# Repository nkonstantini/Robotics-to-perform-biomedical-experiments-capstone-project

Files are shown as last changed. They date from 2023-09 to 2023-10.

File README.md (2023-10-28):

# Robotics-to-perform-biomedical-experiments-capstone-project (PADL v2)
This repository contains all the design files, firmware modifications, and code used for this capstone project in order for you to replicate our work and design your own PADL v2 system.

## Folders:

Build instructions
-  This includes the Bill of Materials used in this project, as well as any tools required.
- This contains the full instructions in order to build this design yourself.

STL files
- This contains all the ready-to-print Fusion360 files we have used in the design.
- Some parts have been sourced from Sukukumar (2023) and [stratop80 (2015)](https://www.thingiverse.com/thing:1071695/files)

CAD files
- This contains all the CAD files we used (.f3d), in case you wish to modify the design. Note that we do not have all the STL files available as CAD files.

Laser cut files
- This contains the file for all the laser-cut parts in 3 different file types (.pdf, .dxf and .cdr)

Marlin firmware
- This contains the necessary instructions to reflash and modify the Marlin firmware on your Ender-3. There is an option to just download the firmware configuration we used if you do not wish to do this yourself.

Python files
- This contains Python files that can generate and export G-code for beginners.
- This contains Python files that can capture the webcam output.

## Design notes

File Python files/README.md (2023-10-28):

# Python code 
- This contains Python files that can generate and export G-code for beginners.
- This contains Python files that can capture the webcam output.

## Download python 3.11.5
https://www.python.org/downloads/ 

## Pip packages to download
Installation notes
To run this notebook you will need to install several packages, including Voila and Pygcode.

1. Voila can be installed via Conda: linked reference
conda install -c conda-forge voila
or with pip:
pip install voila

2. Python-Gcode can be installed via pip only: linked reference
pip install pygcode

3. Python widgets can be installed via pip only: linked reference
pip install ipywidgets

## Overall Flow Chart


## Detailed description
PADL: G-Code Generation Tool, is an innovative solution comprising six distinct components, each equipped with open-source Python code and libraries. The entire toolset is available for download on GitHub, allowing users the freedom to modify and enhance the codebase. This flexibility empowers future capstone students and researchers to update existing code and implement new features, thereby contributing to the continuous improvement of the tool.

0. Set Up
This section provides instructions and resources to set up the environment, including the installation of necessary Python packages such as Voila, PyGCode, and IPyWidgets for the PADL: G-Code Generation Tool (Figure 21).



1. Initialise Input Coordinates
The tool is compatible with all well plate configurations, with the option to input the number of columns, rows, and appropriate spacing between each well. The A1 well plate cell coordinates are measured using the Ender 3 XYZ coordinates, such as A1 = X65 Y154 Z12, prior to the input coordinates step. Additionally, the X step, for example, is measured as 9 (from A2 = X74 Y154 Z12), and the Y step size is measured as -9 (from B1 = X65 Y145 Z12) using the Ender-3 absolute coordinate system. Since equal spacing applies to all well plate cells, coordinates can be derived in subsequent steps. 

The tool facilitates the input of precise coordinates, ensuring accurate positioning, dispensing, and labelling of samples. Researchers can initialise the system for tailored experiments with desired coordinates, such as water reservoir and initial A1 coordinates, as depicted in Figure 22. 

It is worth noting that the use of JSON packages includes the local storage of desired coordinates. Researchers need to set up the coordinates only once, and the information will be automatically saved on their computers. The tool will start from the previously saved coordinates the next time it is opened. Users must refresh the page after making any modifications to ensure they are applied.



2. Speed Settings
A speed slider interface has been implemented, enabling users to control the movement speed of the x-carriage plate when retrieving liquid from the reservoir, the speed when transitioning between different well-plate cells, and the dispensing and aspirating speeds for liquid dispensing and withdrawal, respectively. Additionally, three waiting times have been added: between well-plate cells, between sub-experiments, and the initial waiting time. This control is facilitated using a JSON package as mentioned earlier and illustrated in Figure 23. This feature allows users to adjust the speed parameters for the needles in the syringe pump system, enhancing the precision and efficiency of the PADL system according to specific experimental requirements.



3. Get Well-Plate Coordinates
To optimise sample handling, the tool automatically retrieves well-plate coordinates as shown in Figure 24, from the data provided in Step 1. To verify the accuracy of the generated cooridnates, users must measure the coordinates for well H12. By comparing the actual coordinates to the ones generated automatically, users can confirm if the spacing and initial coordinates have been correctly set up and calibrated. If not, the necessary changes can be made to Step 1. Hence, manual calibration procedures are reduced, reducing manual errors and enhancing the overall efficiency of the PADL system.



4. Establish G-Code Commands for Sample Setup
The tool enables the selection of well-plate cells, displayed as buttons that can be clicked on. For example, a 96-well plate with rows 1-12 and columns A to H will be displayed as 96 buttons. Users can then choose each coordinate in the liquid dispensing order chronologically, visible in the output list box below (Figure 25). Additionally, they can cancel well plate cells by double-clicking. This action will completely remove the coordinates from the list, regardless of their position in the list.



5. Waiting Time Settings for Repeat Lab Work
In a 72-hour experiment, researchers face the task of allocating specific time intervals for sub-experiments. The designated intervals between filling wells serve a vital purpose: they provide sufficient time for the pipetted volume to descend into each well. Furthermore, pauses between sub-experiments are planned to optimise the workflow, especially in repetitive procedures. This feature holds particular significance in cell-culture experiments where the timely replenishment of cell-culture media at consistent intervals is essential. 



6. Tool changing module 
To activate the tool changing module, depicted in Figure 27, a 'Tool Change' button has been introduced, as illustrated in Figure 28. Users can press this button to switch the tool and initiate another task with a different tool.



7. Save Python G-Code and Export as a .gcode File
Upon completion of the setup, the tool enables users to save the generated G-code, as illustrated in Figure 28. Additionally, the tool provides an option to export the G-code in .gcode format in the same folder as the Python script when the ‘Send to PADL G-code’ button is clicked. This ensures compatibility with the PADL firmware, as 3D printers can only run .gcode files, and eliminates the need for manual copying and pasting. The generated file can be operated through the microUSB cable connecting the computer to the modified Ender-3 printer via slicer software such as Repetier-Host, or copied to the microSD card using the computer. The microSD card can then be inserted directly into the microSD card port for direct operation.



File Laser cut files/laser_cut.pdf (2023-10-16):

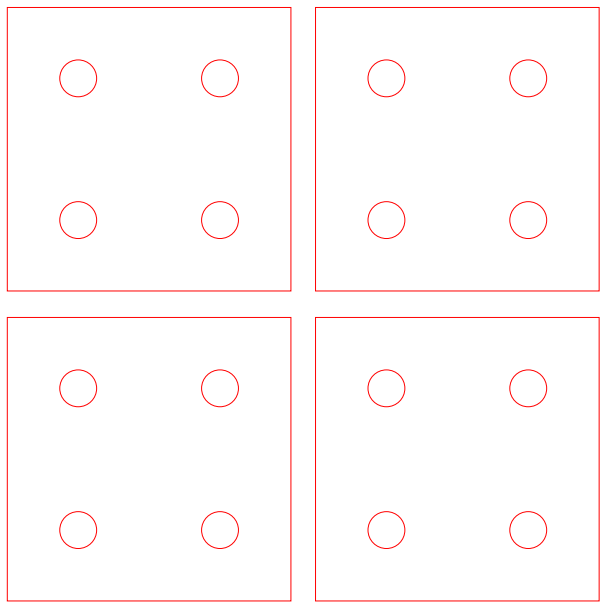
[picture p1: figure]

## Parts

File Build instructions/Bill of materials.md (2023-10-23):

## Table 1: Bill of materials used for the final design (Sukukumar, 2023)

| Category     | Item | Description    | Quantity | Supplier | Cost ($) |
| :---:        |    :----:   |       :---: |  :----:   |   :----:   |  :----:   |  
**Original (Sukukumar’s) design** | Ender-3 | Creality Ender-3 Desktop 3D Printer Kit | 1 | InkStation Australia | 219
| | Stepper Motor | Stepper motor 42-34 (Motor size: 42 * 42 * 34 mm) for Ender-3 | 1 | 3DPO Online | 24.95
| | V-Rail | V-slot 40x40mm, 1m length | 1 | Maker Store | 35.85
| | M5 Lead Screw | Stainless steel threaded rod | 1 | Bolts & Industrial supplies | 24.76 |
| | M5 nut | (For use in syringe pump) | 1 | Telstra Creator Space (TCS) | -
| | Shaft coupler | 5 to 5mm, 20mm outer diameter, 25mm length | 1 | Bilby 3D | 9
| | Extruder carriage | Ender-3 hotend carriage with wheels | 1 | AliExpress | 13.89
| | M5x40 screws | | 4 | TCS | -
| | M3x10 screws | | 4 | TCS | - 
| | Springs | Creality Ender-3 steel heatbed springs | 4 | Ebay | 5.99
| | Tube | Syringe tube, 75cm microbore extension length | 1 | Joya Medical Supplies | 1.50
| | Disposable Syringe | Disposable syringe size: 5, 10 and 20 mL | 3 | Laboratory | -
| | Needle | 8Gx1.5” | 3 | Laboratory | -
| | M3 counter-sunk screw | | 2 | TCS | -
| | 96-well plate | Costar | 1 | Laboratory | -
| | Magnets | Neodynium disc magnets, 5x2mm | 4 | Ebay | 10
| | Isopropyl alcohol | | |-| Laboratory | -
| | Superglue | | | -| TCS | -
| **Updated design** | microSD card | 8gB | 2 | Ebay | 7.98
| | GT2 timing belt | 6mm width, 2mm tooth pitch, rubber, 1m length | 1 | Aus3D | 3.95
| | Stepper Motor | Stepper motor 42-34 (Motor size: 42 * 42 * 34 mm) for Ender-3 y-axis | 1 | 3DPO Online | 23.95
| | Capacitor | 100µF, 35V or 50V rating | 1 | TCS | -
| | Dupont wires | Male-male | 10 | TCS | -
| | Dupont wires | Female-male | 4 | TCS | -
| | TMC2208 Stepper motor driver | MPN 1x | 2 | Ebay | 25.90
| | PCB Soldering board | 5x5cm | 1 | TCS | -
| | Extension screen cable | For Ender-3, 200cm length | 1 | Amazon AU | 7.99
| | Extension power cord | XT60, 14AWG, 30cm length | 2 | Ebay | 24
| | GT2 belt timing pulley | 16T, 6mm belt size, 5mm bore hole diameter | 3 | Ebay
| | Incubator water tray | Kitty litter tray 44x31x7.5cm | 1 | Big W | 4.5
| | Webcam | HD Wifi Camera 1080P Surveillance Security Outdoor Sport Camera | 1 | Kogan | 25.37
| | Heat sink | Copper | 3 | - | -
| | Double-sided tape | (for attaching heat sink to stepper motor and acrylic plates to tool mount) | - | Laboratory | -
| | Powerbank | 10,000mAh | 1 | Officeworks | 39
| | Neodymium magnets | N38, 7x3mm disc magnets | 20 | AMF Magnets | 20.80
| | Grub screws | M4, 10mm length | 4 | Bolt and Nut | 10
| | Conductive grease | CRC di-electric grease 14.2G | 1 | Repco | 17
| | Printed circuit board lacquer | Clearcote Circuit Board Lacquer spray (175g aerosol) | 1 | Chemtools | 13.75
| | Chemical resistance gloves | Alphatec Butyl Black Gloves, size 8 | 1 | Blackwoods | 52.16
| | MicroUSB cord | 1m | 2 | Ebay | 6.39
| | Aluminium tape | 30cm (for waterproofing motherboard) | - | TCS | -
| | M5x70 screws | (for mounts) | 2 | TCS | -
| | M5x100 screws | (for screwing in frames to Ender-3) | 7 | TCS | -
| | M6 nutsert | (for spacing stepper motor frame) |3 |TCS|-
| |M6 washers|(for mounts, frame)|22|TCS|-
| | M5 nut| Nyloc|2|TCS|-
| | M4 nut|(for securing waterproof case)|3|TCS|-
| | M4 washers|(for securing waterproof case)|3|TCS|-
| |M4x10 screws|(for securing waterproof case)|3|TCS|-
| | M3x16 screws|(for screwing in new stepper motor)|4|TCS|-
| |M5x50 screws|(for screwing in stepper motor mount)|4|TCS|-
| | Electrical tape|(for pcb lacquer application and to seal off wires in incubator)|1m roll|TCS|
| | Blunt needle|8Gx1.5” (for applying the conductive grease to the ports) |1|Laboratory|-
| | Zap-A-Gap Bonder| (for gluing in magnets and syringe mount into tool mount)|1|TCS|-
| |Garbage bags|Large, black, polyethylene|2|Laboratory|-
| |Polylactic acid (PLA) spool|1.75mm diameter, orange, PLA+ filament|1kg|eSUN|39.95
| | Trefolex cutting compound|For tapping holes|1|TCS|-
| | Hygrometer|Measures temperature and humidity|1|Ebay|8.99
| | | | |**Total cost**| **$676.62**

_Note: TCS is a university workshop_ 

## Table 2: List of tools used for the final design
|Tool|Description|
| :---:  | :---:  |
|Drill and drill bits|To drill holes into the V-rails for assembly
Tapping set|To thread holes to screw parts together, including metallic and 3D-printed parts
Laser-cutting machine|To create the acrylic components
Metal bandsaw |To cut v-rail down to size
3D printer|To create the 3D-printed components
|Soldering iron, solder flux, wire stripper|To solder the electrical circuit that controls the added stepper motor
Scissors|To cut the belt down to size, and to cut tape 
Allen keys|To fasten or secure screws
Fumehood|To safeguard against aerosol fumes generated from spraying PCB lacquer

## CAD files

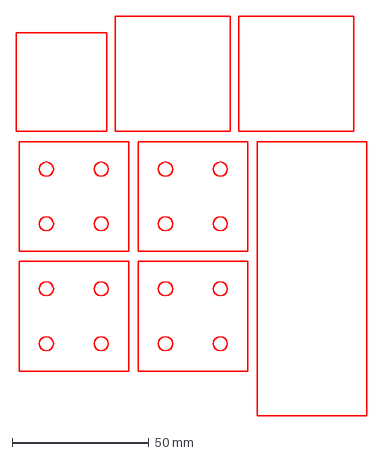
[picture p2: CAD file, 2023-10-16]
Laser cut files/laser_cut.dxf
128.0 x 145.7 mm

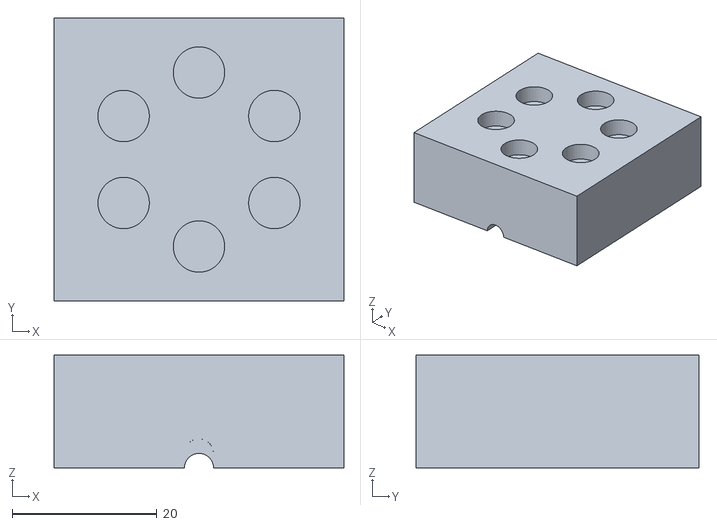
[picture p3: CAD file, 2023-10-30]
STL files/Tool change - six magnets.stl
40.0 x 39.0 x 15.6

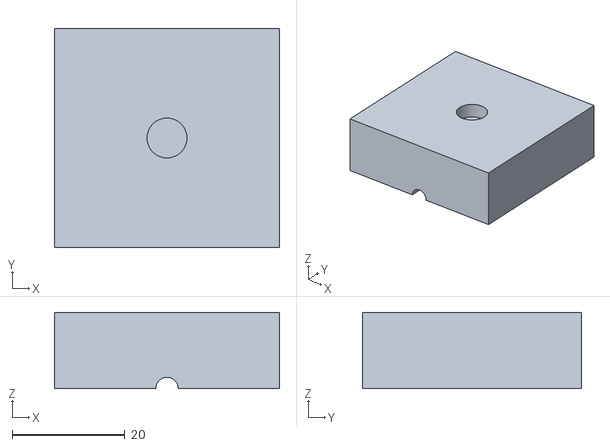
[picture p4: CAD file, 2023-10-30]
STL files/Tool change - one magnet.stl
40.0 x 39.0 x 13.6

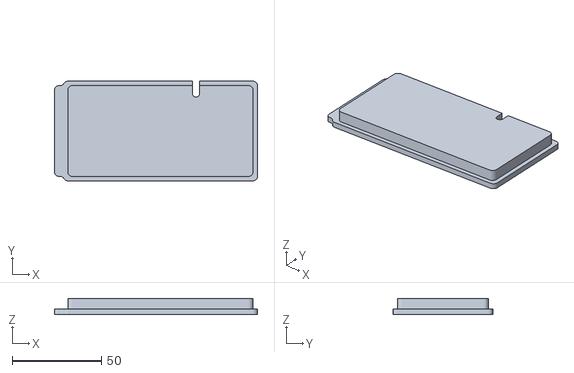
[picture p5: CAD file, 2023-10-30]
STL files/Waterproofing case - TPU lid.stl
114.0 x 56.0 x 9.00

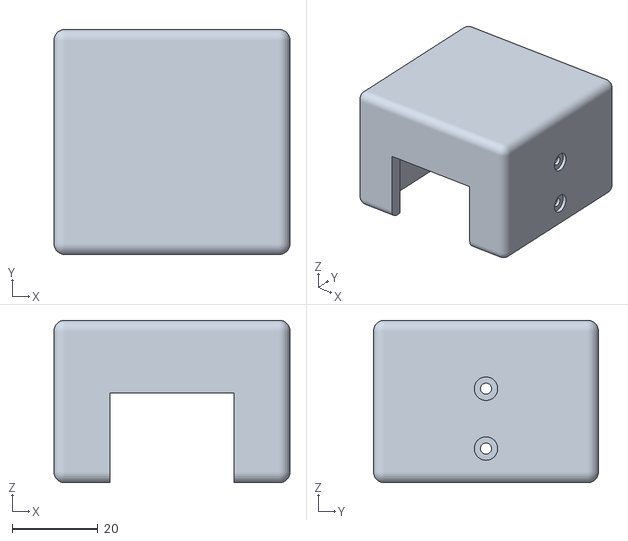
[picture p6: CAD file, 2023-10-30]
STL files/Tool Change - Clamp.stl
55.2 x 52.6 x 38.0

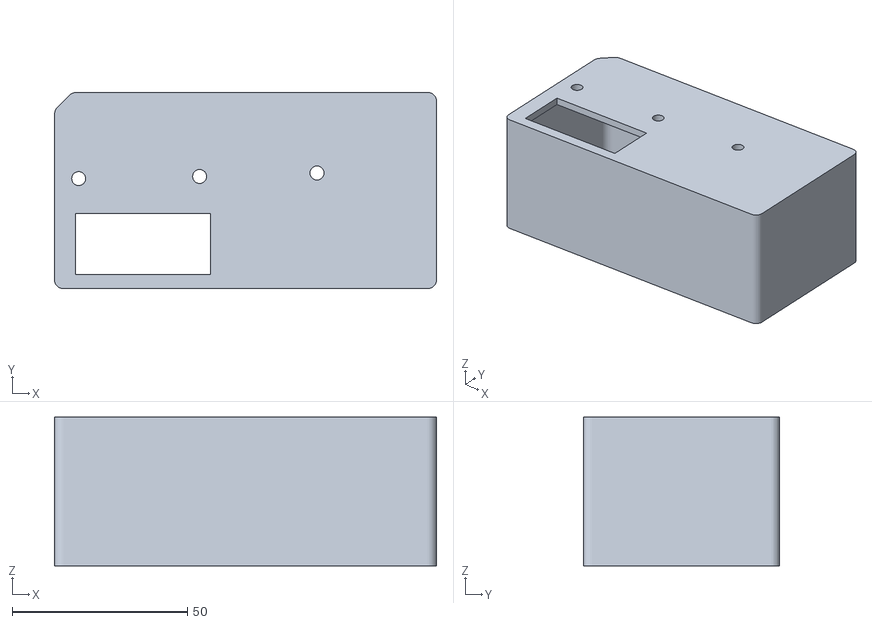
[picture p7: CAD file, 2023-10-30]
STL files/Waterproofing case - PLA case.stl
109.0 x 56.0 x 42.5

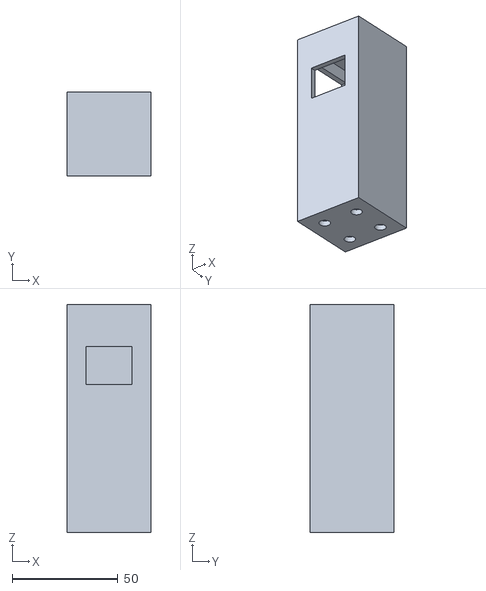
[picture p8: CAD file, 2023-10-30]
STL files/Waterproofing - soldered board case.stl
40.0 x 40.0 x 108.0

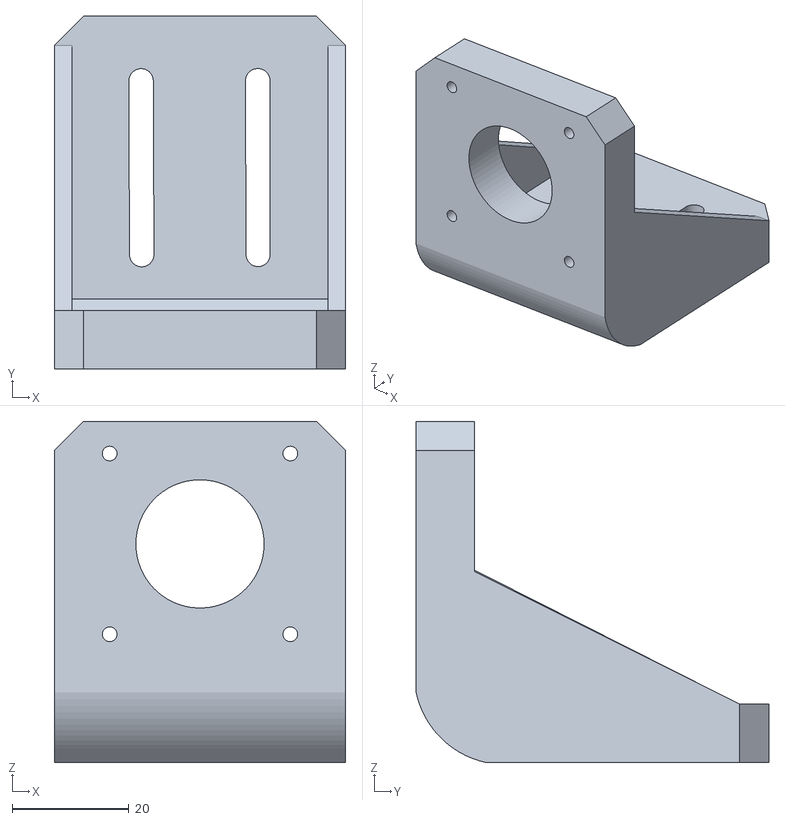
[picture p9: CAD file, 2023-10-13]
STL files/A_axis_stepper_motor_mounting_bracket.stl
50.0 x 60.5 x 58.5

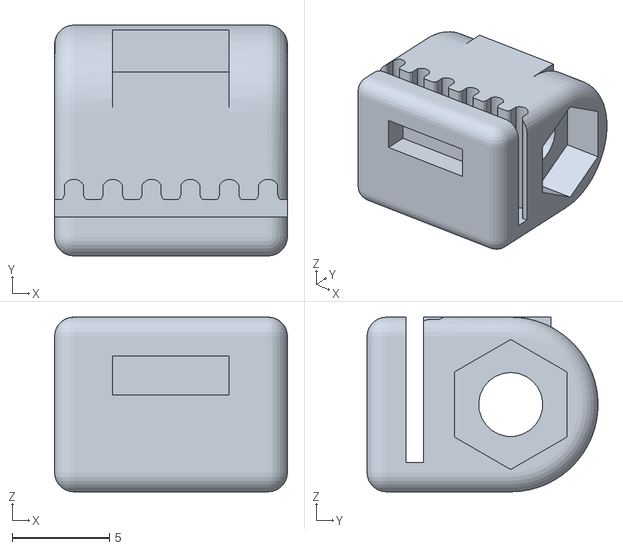
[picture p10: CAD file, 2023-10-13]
STL files/GT2_belt_tensioner_body-1.STL
12.0 x 11.9 x 9.00

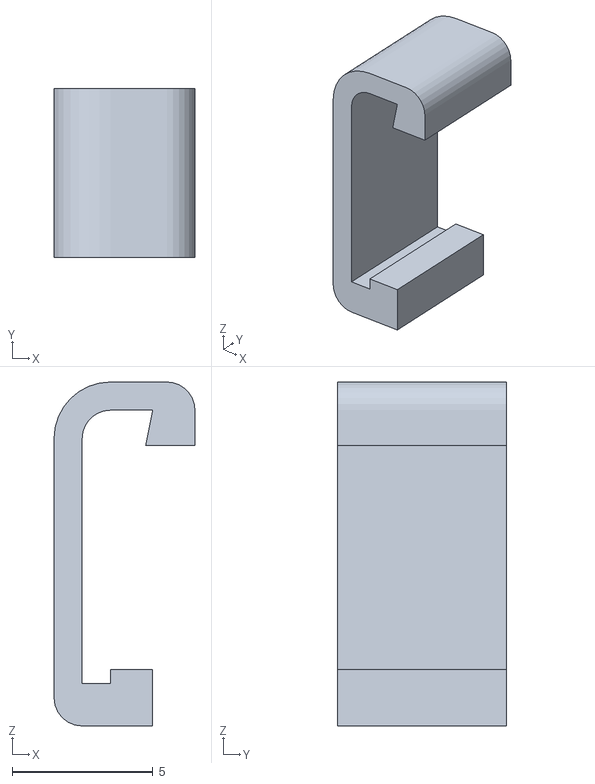
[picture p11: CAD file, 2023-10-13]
STL files/GT2_belt_tensioner_clip-1.STL
5.00 x 6.00 x 12.2

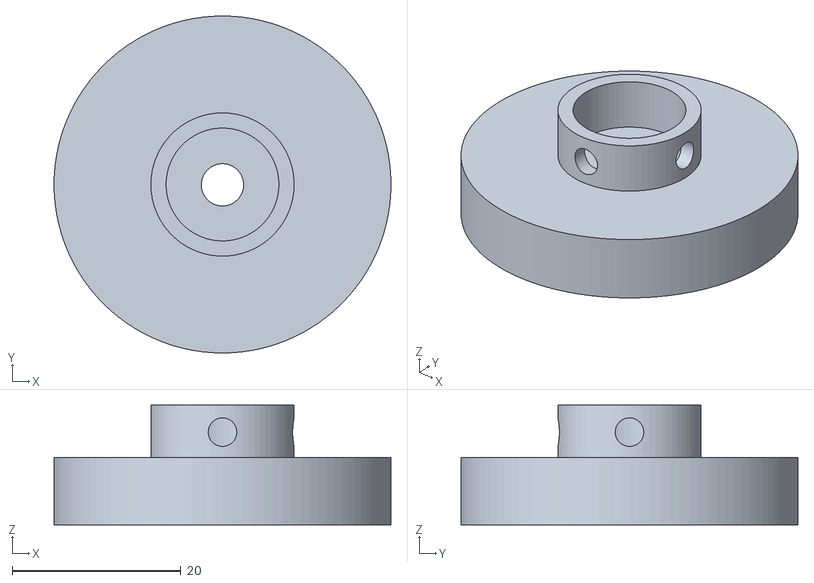
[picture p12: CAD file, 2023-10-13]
STL files/Tool change - tool mount three magnets.stl
40.0 x 40.0 x 14.2

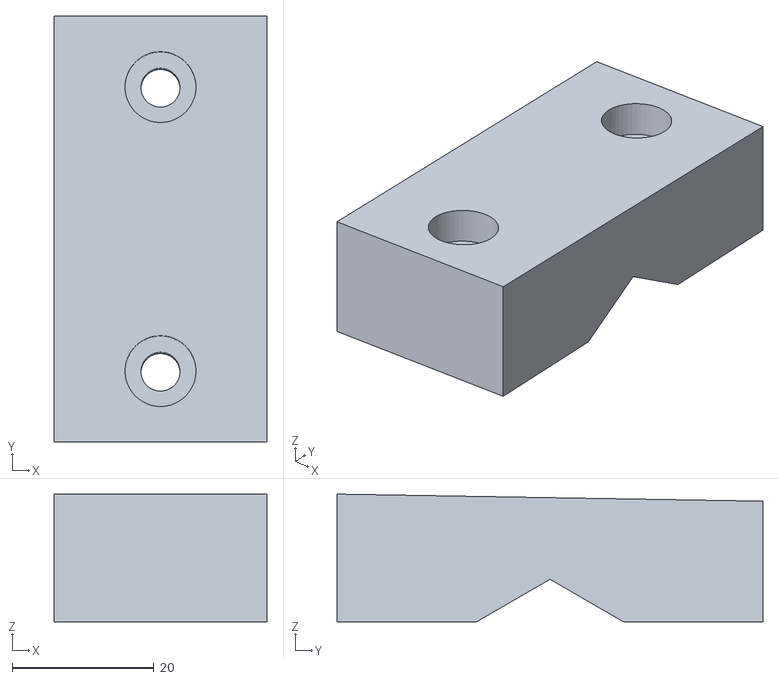
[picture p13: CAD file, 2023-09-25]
STL files/Syringe End Mount Clamp.stl
30.0 x 60.0 x 18.0

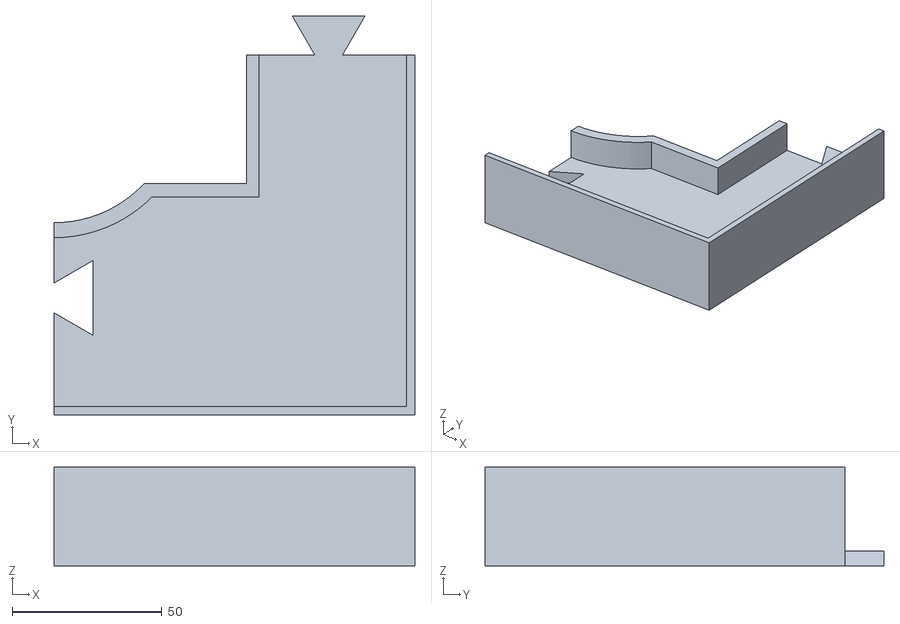
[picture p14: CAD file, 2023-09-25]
STL files/Platform Wellplate part 1.stl
120.5 x 133.3 x 33.0

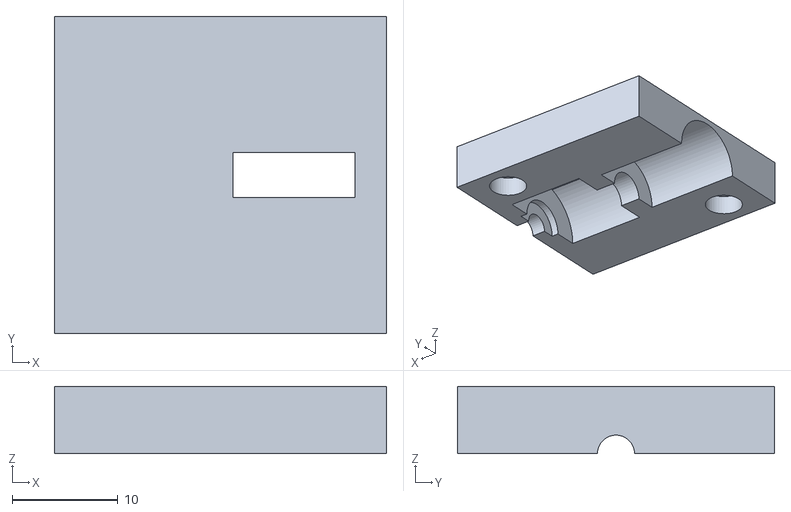
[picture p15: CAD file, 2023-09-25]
STL files/Tube Holder Top part.stl
31.4 x 30.0 x 6.35

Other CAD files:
STL files/Platform Wellplate part 4.stl
STL files/Platform Wellplate part 2.stl
CAD files/A_axis_stepper_motor_mounting_bracket.f3d
CAD files/Tool change - Clamp.f3d
CAD files/Tool change - one magnet.f3d
CAD files/Tool change - six magnets.f3d
CAD files/Tool change - tool mount three magnets.f3d
CAD files/Waterproofing - soldered board case.f3d
CAD files/Waterproofing case - PLA case.f3d
CAD files/Waterproofing case - TPU lid.f3d
STL files/Clamp Bar Short.stl
STL files/Dovetail Cap.stl
STL files/Platform Wellplate part 3.stl
STL files/Slide Carraige Plate.stl
STL files/Slide Mount.stl
STL files/Stepper Motor End Mount.stl
STL files/Syringe End Mount.stl
STL files/Tube Holder Bottom part.stl

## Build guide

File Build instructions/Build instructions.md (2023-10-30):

# Build instructions for the PADL v2 system


# Part 1: Assembling Ender-3 3D Printer
Please consult the included instructions from Creality with your printer.

# Part 2: Assembling the syringe pump and well-plate frame
The instructions for this part have been taken directly from Sukukumar (2023).

Reference: Thusya Sukukumar. (2023). *_Development of an open-source, multifunctional liquid handling robot for tissue engineering applications_*. RWTH Aachen University.

**Build instruction overview**




**Step 0: Prepare, Purchase, and 3D print**

Before starting the assembly process, purchase additionally to the Ender-3 DIY 3D Printers Kit, the other components for PADL, which are listed in the Bill of Materials, and 3D
print the parts listed in the design file summary. Another option is that the Ender-3 itself
can print the CAD parts before modifying them into a liquid handler if another 3D printer
is not accessible.
The tools necessary for this modification process were, for the most part, provided by
Creality, Shenzen, China. Additionally, is Isopropyl alcohol (IPA), a Q-tip, Super glue,
and tweezers required (see Fig. 1)



**Step 1: Assemble the Ender-3 3D printer**

Start with assembling the Ender-3 3D printer according to the Shenzen Creality 3D Technology guide. Detailed instructions for assembly and use are available on the TF card
provided by the manufacturer.
After assembling the 3D printer, loading the filament, and leveling the wheels and bed
as recommended by the manufacturer, install the software, and prepare to print any of
the G-code files, which the manufacturer loaded onto the TF card. No troubleshooting is
required if the 3D printer functions according to the manufacturer’s specifications. If the
CAD parts are already 3D printed, the modification of the Ender-3 into a PADL can start.
NOTE 1 The power cable the manufacturer provides can have a loose connection, as
shown in Fig. 1a. Replace (Fig. 2b) the power cable with an Australian 3-pin (rating: 10
A at 250 V AC) male connector and an IEC-C13 female connector from a different manufacturer. 



NOTE 2 Another possible manufacturer's error is a misaligned Ender-3 frame. The unlevelled frame leads to the inaccuracy of the liquid handler. One solution is to loosen up
one or both M5 screws (circled in yellow), rearrange the base rail until the frame is
aligned, and finally, tighten it again.



**Step 2: Modifications to the Ender-3 motherboard**

Before starting the modification process, turn off the Ender-3 and remove the power cable.
Figure 4 gives an overview of the motherboard of Ender-3. The motherboard provides
connectivity between all the hardware components and moves power to them. The labels
in Fig. 4 on the motherboard refer to the plugs occupied for the 3D printer function.



Step 2.1: Open the electronic box

The motherboard is in the electronic box under the hotbed. To open the electronic box,
remove the three M3 screws (circled in yellow in figure 5) on the cover of the motherboard
by using the hex key. Lift the cover carefully (NOTE 1).
To altogether remove the motherboard cover, follow Step 2.2.

Step 2.1: Open the electronic box

The motherboard is in the electronic box under the hotbed. To open the electronic box,
remove the three M3 screws (circled in yellow in figure 5) on the cover of the motherboard
by using the hex key. Lift the cover carefully (NOTE 1).
To altogether remove the motherboard cover, follow Step 2.2.



NOTE 1 Be careful while removing the cover of the motherboard. The motherboard fan,
which is attached to the other side of the lid (see figure 17), is plugged into the motherboard, and a forced pull while removing the cover can cause damage to the fan cables.

Step 2.2: Remove the motherboard cover

To remove the motherboard cover altogether, unplug the motherboard fan connector
from the motherboard. The connector is plugged into the controllable motherboard fan
port (see Fig.4). First, remove the hot glue carefully from the connection (NOTE 2). Unplug the motherboard fan connector, carefully remove the motherboard fan, and set it
aside.

NOTE 2 Be gentle while removing the hot glue from the connectors. It is recommended
to use isopropyl alcohol (IPA) on a q-tip. Rub the IPA around the edges of the hot glue
and remove the hot glue with tweezers.

Step 2.3: Remove the redundant cables

In this Step remove all the remaining connectors and cables which are marked with a
red cross in figure 6. The cables connected to the white ports can be removed like the
motherboard fan connector as in Step 2.2. For cables connected to the green ports, first,
unscrew the two screws on top of the port (the screws do not need to be removed). After
a few turns of the screws, the cables can be easily pulled out. Also, the cables which are 
plugged into the ports marked with a replacement sign can be removed in this Step. The
replacement of this cable will be explained in Step 4.5. 



**Step 3: Remove the extruder from the X-axis carriage plate** 

For PADL, the extruder is replaced by a syringe pump (Step 7). One can access the
extruder by removing the housing (Step 3.2). Figure 7 shows the extruder fan housing.



Fig 7: Overview of the extruder

NOTE 1 The extruder assembly with the Stepper motor does not need to be removed,
although it has no function for PADL. This makes it easy for the liquid handler to remodify
into a 3D printer.

Step 3.1: Unscrew the Bowden tube

Remove the Bowden tube from the extruder assembly (see Fig. 8a) by unscrewing the
pneumatic connector (circled in yellow) like in Fig. 8b. 



Step 3.2: Unscrew the extruder fan housing

To detach the extruder fan housing (NOTE 2) from the X-axis Carriage Plate, remove
the two M3 screws on the housing. 



NOTE 2 Do not pull on the extruder fan housing because it can cause damage to the
cables. Figure 9b shows that it is impossible to remove the fan housing completely without removing the extruder.

Step 3.3: Remove the extruder

To remove the extruder from the carriage plate, unscrew the two M3 screws on the extruder (see Fig. 10). Set the extruder aside (see Fig. 11).





Step 3.4: Pull out the extruder cables

The last Step to altogether remove the extruder is to remove the cables in the electronic
box, which are already unplugged (Step 2.3). For this Step, approach the Ender-3 from
the rear (see Fig. 12). First, carefully cut the zip tie, which connects the four cable assemblies (multiple cables arranged into a single unit). Secondly, carefully pull the extruder cable assembly. After the cables are pulled out successfully, the extruder can be
set aside. 



NOTE 3 Be careful while pulling the extruder cable assembly. The cables can be tangled
in the electronic box, and a forced pull can damage the cables.

**Step 4: Cutting process (Outsource)**

To prepare the modification of the Ender-3 into PADL, three parts must be altered. It is
recommended to outsource these tasks. If the expertise and tools are available, the user
can perform Steps 4.1 to 4.5.

Step 4.1: Cut V-slot rail to size

Cut the V-slot rail to size, as suppliers commonly don’t provide the correct size. Cut the
V-slot rail to 300 mm. The rail is provided with threaded holes at both ends. However,
the threaded holes must be redone on the cut end after cutting the rail at one side. Cut
M5 internal metric threads into the four holes on the cut end to 25 mm (see Fig. 13).

NOTE 1 If the user does the cutting process, wear appropriate personal protective equipment when using cutting tools.



Step 4.2: Cut the lead screw to size

Cut the M5 lead screw to size, as suppliers commonly don’t provide the correct size. Cut
the lead screw to 270 mm.

NOTE 2 If the user does the cutting process, wear appropriate personal protective equipment when using cutting tools.

Step 4.3: Grind down the two M3 countersunk screw head

This Step is a preparation for Step 9. In Step 9 the Tube Holder will be attached to the
X-axis Carriage Plate. The Tube Holder exits from two parts, which are magnetically
attached. To enable the top part's attachment to the Tube Holder's bottom part (see Fig.
14b), the surface of the bottom part needs to be flat. Figure 14a compares an M3 hex
screw and a ground M3 countersunk screw screwed to the bottom part of the Tube
Holder.
The two M3 countersunk screw heads need to be grind down to a diameter of 4.5 mm
with a tolerance of ± 0.15 mm (NOTE 3). 



NOTE 3 M3 countersunk screws have, according to DIN 7991, a head diameter of a
minimum of 5.54 mm and a maximum of 6.72 mm.

Step 4.4: Cut an opening in the motherboard cover

This Step is a preparation for Step 10. In Step 10, the position of the Z-limit switch will
be adjusted. This alteration leads to the manufacturer's opening for the cable not being
used because otherwise, there is increased tension on the wires of the Z-limit switch and
prevents the motherboard cover from closing. Therefore, an altered wire opening is required to cut.
Unplug the connector and remove the motherboard cover (Step 2.2). Cut the opening at
a distance of 20 mm from the Ender-3 opening, as shown in the figure. The dimensions
of the opening are a length of 14 mm and a width of 6 mm. The dimensions for the altered
opening are shown in figure 15. 



NOTE 4 During the cutting process, ensure the fan on the rear side is not damaged.

NOTE 5 If the cutting process is done by the user, make sure to wear appropriate personal protective equipment when using cutting tools

Step 4.5: Rewire the motherboard fan. **_Note: Step 4.5 is not required for the updated design. The fan can be removed completely from the motherboard and discarded_**

As mentioned in the previous Step (Step 2.3), the extruder fan port in the motherboard
has been replaced; therefore, the motherboard fan needs to be modified to enable the
plugging into the extruder fan port. The modification is illustrated in figure 18.

The reason for plugging the motherboard fan into the extruder fan port is that the motherboard fan function is connected to the part cooling fan, which is redundant for the PADL
version. So, if the part cooling fan is not working, the motherboard fan will not work. Not
cooling the motherboard will eventually damage it. A solution is to plug in the motherboard fan to the extruder fan port as it works without exception and the extruder fan is
redundant for PADL.

Step 4.5.1 Cut the connector of the motherboard fan

To connect the motherboard fan to the extruder fan port, remove the JST-HX-style connector motherboard fan cable (see Fig. 19a). Strip 2.5 cm of the insulation off the end of
each wire.



NOTE 6 If the user does the cutting process, wear appropriate personal protective equipment when using cutting tools.

Step 4.5.2: Thin the wire ends 

To hold the fine wire ends together after removing the JST-HX-style connector it is recommended to thin the ends using a soldering iron. Figure 19b shows the two thinned
ends of the motherboard fan wires. 



NOTE 7 If the user does the thinning process, wear appropriate personal protective
equipment when using soldering tools.

Step 4.5.3: Connect the motherboard fan wires to the extruder fan port

This is the last Step on the main board. Loosen the two screws on the top of the extruder
fan connector and insert the wires (NOTE 8). Tighten the two screws and check that the
wires are still plugged in by gently trying to pull them out.
Figure 19 shows the motherboard with all the cables for the PADL plugged in and the
motherboard fan cable replaced by an extruder fan cable.
The motherboard cover will be closed in Step 10. 



NOTE 8 It is important to insert the wires (red and black) to correct plugs as illustrated in
figure 18.

**Step 5: Replace the Hotbed leveling springs (keep the springs for Step 7.7) with the
yellow springs**

The yellow replacement springs (see Fig. 20b) are more rigid than the springs supplied
by the manufacturer (see Fig. 20a), which reduces the hotbed's vibration and increases
the positioning accuracy. In addition, the shape of the replacement springs is flat at the
top and bottom, unlike the manufacturer's springs, which are rounded. This results in the
hotbed being flat against these compression springs and less movement or shifting of
the springs during the dispensing process.
The manufacturer's springs are reused for the syringe pump in Step 7.7.



Step 5.1: Remove the manufacturer’s springs (Obtaining the springs for the syringe pump clamp mechanism)

To remove the old manufacturer’s springs, loosen the four hotbed adjustment wheels
clockwise (see Fig. 21). Start with the front two wheels simultaneously by turning them
until they can be entirely removed. Repeat this for the two wheels at the back. Set the
four wheels aside.



Step 5.2: Remove the hotbed

Lift the hotbed of the Y-axis carriage plate and set it aside, as shown in Figure 22. Remove the manufacturer’s four springs and obtain one of these springs for the syringe
pump clamp mechanism (NOTE 2). The spring will be needed in Step 7.7.



NOTE 1 Use caution when removing the heater bed, as the heater wiring is located in
the rear left corner.

NOTE 2 Only one of the four springs is needed for the syringe pump clamp mechanism.
The other three can be used as replacements.

Step 5.3: Insert the yellow springs

To insert the yellow springs, set three out of four springs right above the holes of the Yaxis Carriage Plate as shown the Figure 23, and insert the fourth spring onto the screw
in the back-left corner and insert on top of it the hotbed cable strain relief. The following
action is to lift the hotbed with the inserted screws, set it down on top of the springs and
make sure the four screws of the hotbed are inside the springs (see Fig. 24, NOTE 3).
Put the screws down the screw holes of the Y-axis Carriage Plate. 



NOTE 3 The springs may fall off when placing the hotbed on the Y-axis Carriage Plate.
Make sure that the springs are inserted into the screw.

Step 5.4: Reattach the adjustment wheels

After the hotbed is placed on top of all four springs, reattach the hotbed adjustment
wheels and tighten the wheels anticlockwise. Start with the two wheels at the front, as
shown in Figure 24; however, do not tighten these yet. Put the two wheels at the back
first on. After all four wheels are attached, start tightening the front two wheels down and
repeat this for the back two wheels.



Step 5.5: Level the hotbed

After all four wheels are tightened up all the way down, level the hotbed as in Step 1
according to the manufacturer's (Creality) specifications.
Step 6: Remove the POM wheels from the substitute extruder carriage
The POM wheels are utilized in a further Step (Step). Therefore, the wheels are removed
from the extruder carriage plate. The POM wheels are shown in Figure 26b.
Unscrew the three M3 screws (circled in yellow in Figure 26a) and save the three screws,
three POM wheel bearing pulleys, three anti-loosening nuts, two spacers, and the eccentric hexagonal adjuster (shown in Fig.).

NOTE 4 The extruder carriage plate can be used as a substitute.





**Step 7: Assemble the open-source syringe pump** 

The Syringe Pump is based on Baas et al. open-source project. However, some changes
have been made. Compared to Baas et al., this syringe pump enables aspirating in addition to dispensing of liquid. Baas et al. syringe pumps can only dispense liquid with a
maximum dynamic viscosity of 250 mPas. The PADL Syringe Pump can dispense liquids
with a maximum dynamic viscosity of 500 mPas.

Step 7.1: Layout Syringe Pump

Start with laying out all the parts needed to build the open-source syringe pump. All
components used in the syringe pump system are shown in Figure 28. 



Step 7.2: Install the Syringe End Mount

First, install the Syringe End Mount to the rail which was cut to size in Step 4.1. Slide the
mount onto the rail (see Fig. 29a) and use two M5 x 40 mm screws to fasten it (see Fig.
29b). 



Step 7.3 Mounting wheels on the Syringe Carriage

First, take the two 3D printed parts, Slide Mount and Slide Carriage Plate. Fit the Slide
Mount onto Slide Carriage Plate as shown in Fig. 30. Now, the parts (M5 bolts, shafts,
eccentric hexagonal adjuster, POM wheels, and nuts) needed, which were removed from
the substitute extruder carriage in Step 6. Insert the three M5 bolts into holes of both
parts in conjunction (see Fig. 31A). Turn around the Slide Mount and Slide Carriage Plate
facing with the rear and insert the other parts in the following order: spacer or eccentric
hexagonal adjuster (as in Fig. 31A, NOTE 1), POM wheels (see Fig. 31B) and nuts (see
Fig. 31C). Tighten the bolds by holding the nuts with a wrench and screw the bolt onto
the nut with a hex key. 





Fig. 31: Mounting the Syringe Carriage with spacer/eccentric hexagonal adjuster (A),
POM wheels (B), and nuts (C).

NOTE 1 The eccentric nut needs to be inserted on the bolt as shown in Figure 31C,
otherwise, the rail guidance mechanism will fail.

NOTE 2 The eccentric hexagonal adjuster will be later used to remove slop in the rail
guidance mechanism. 

Step 7.4: Insert the Syringe Carriage on to the rail

Slide the Syringe Carriage onto the rail. Figure 32a shows that the carriage may indicate
a slop in the rail guidance mechanism, which can cause the carriage not to move or not
to slide effortlessly onto the rail. One solution is to adjust the tension of the wheels by
turning the eccentric hexagonal adjuster (see figure 32b). Figure 32c shows a mounted
syringe carriage on the rail.

NOTE 3 An indication of misalignment is the wheels not being parallel, as shown in figure
32a.



Step 7.5: Install the Stepper End Mount

Install the Stepper Motor End Mount using M5 x 40 mm screws. Slide the mount onto
the rail (see Fig. 33a) and fasten the screws (see Fig. 32b). 



NOTE 4 The Syringe Carriage must already be sided onto the rail (Step 7.4) before installing the Stepper End Mount.

Step 7.6: Install the Stepper motor on the Stepper Motor End Mount

Four M3 x 16 mm screws are required to install the Stepper motor. Place the Stepper
motor onto the Stepper Motor End Mount, as shown in Fig. 34 (NOTE 5). Position the
four screws in the holes, as shown in Figure 35a, and fasten the screws onto the Stepper
motor (see Fig. 35b).



Fig. 34: Stepper motor placed onto the Stepper Motor End Mount

NOTE 5 The Stepper motor connector should face the correct direction, as represented
in Figure 34 by an arrow.



Step 7.7: Install the Syringe clamping Mechanism

The Syringe Clamping Mechanism is designed to prevent the syringe from moving. This
mechanism consists of a Clamp Bar, a spring (collected in Step 5.1), and a Dovetail Cap
(see Fig. 36). Clamp Bars are available. They can be changed to accommodate different
syringe diameters. Slide the Clamp Bar into the slot on top of the Syringe End Mount,
followed by the spring (see Fig. 37a). Secure the Syringe Clamping Mechanism by closing the slot with the Dovetail Cap (see Fig. 37b)





Step 7.8: Assemble leadscrew-and-nut system

The leadscrew-and-nut system enables the syringe plunger to be pushed or pulled so
that the liquid can be dispensed or aspirated. The rotational movement of the leadscrew
is translated into a linear movement via the leadscrew-and-nut system.

Step 7.8.1: Insert leadscrew through the Syringe End Mount
Slide the leadscrew (cut to size in Step 4) through the Syringe End Mount, up to the
Syringe Carriage (see Fig. 38).



Step 7.8.2: Insert M5 nut into the Syringe Carriage

Fix the leadscrew to the Syringe Carriage using an M5 nut. Lay the assembly with the
inserted leadscrew on its side and push in the M5 nut (see Fig. 39a, NOTE 6), centering
it with the trough-hole for the leadscrew. As shown in Fig. 39c, thread the leadscrew
through the M5 nut.



NOTE 6 To push the nut it is useful to use a hex key (see Fig. 39b)

Step 7.9: Install the shaft coupler

The shaft coupler is a mechanical component that connects the Stepper motor and leadscrew. It transmits the rotational movement of the motor to the leadscrew.
Install the shaft coupler onto the Stepper motor by tightening the two grub screws (circled
in green in Fig. 41a and 41b). Thread the leadscrew up to the shaft coupler (see Fig. 40).
To connect the leadscrew to the shaft coupler, tighten the other grub screws (circled in
orange in Fig. 41a and 41b, NOTE 7). 





NOTE 7 Rotate the shaft coupler to reach the two grub screws on the other side.

Step 7.10: Install the Syringe Clamp Fastener (for high viscosity liquids)

The Syringe Clamp Fastener secures the syringe in addition to the Syringe Clamping
Mechanism (spring). Especially when dispensing liquids with higher viscosity, this clamp
prevents the disposable syringe from bending for liquids with a maximum dynamic viscosity of 500 mPas.
NOTE 8 Without attaching the Clamp Fastener, the syringe barrel is only secured by the
Syringe Clamping Mechanism. Then the Syringe Pump can dispense liquids with a maximum dynamic viscosity of 250 mPas without error.
Step 7.10.1: Attach the Clamp Fastener to the Syringe End Mount
Insert the two M5 x 40 mm screws, which are partially threaded, into the holes in the
Clamp Fastener, and then insert the Clamp with the two screws into the holes at the top
of the Syringe End Mount (see Fig. 43, NOTE 9).



NOTE 9 Do not completely tighten the Clamp Fastener to the Syringe End Mount

Step 7.10.2: Fasten the Syringe

Insert the syringe into the Syringe Pump as shown in Fig. 44(A). Push the clamp down
till it touches the syringe (see Fig. 44 (B)), and finally, tighten the two M5 screws until the
syringe is secured (see Fig. 44 (C), NOTE 11).



Fig. 44: Clamp process with Syringe Clamp Fastener: (A) Insert Syringe, (B) Push Fastener down, (C) Tighten screws
Some elements from the Ender-3 will be extracted during the build Steps. It is recommended to keep these parts safe, as there is always the possibility of converting PADL
back to Ender-3.

**Step 8: Connect the syringe pump to the Ender 3**

The extruder (E) of the Ender-3 is redundant for PADL. Therefore, the E-cable can be
unplugged from the Stepper motor (other end is still plugged into the motherboard) and
plug it into the Stepper motor of the syringe pump.

Step 8.1: Remove the connector from Extruder Stepper Motor

To remove the E-cable from the Stepper motor (Fig. 45b), pull the connector (circled in
yellow in Fig. 45a) attached to the motor.



NOTE 1 The orange label (see Fig. 45a circled in yellow) on the cables indicate in which
Stepper motor or limit switch the cable is plugged into. The E on the yellow circled cable
marks the Extruder cable.

Step 8.2: Connect the E-cable to the syringe pump

Position the Syringe Pump on the left side of the Ender-3 as shown in Fig. 46. Insert the
connector, which was removed in Step 8.1, into the Stepper motor of the Syringe Pump. 



**Step 9: Install tube and Tube Holder**

An extension tubing with a female luer lock to a male luer lock transports the liquid from
the Syringe Pump to the platform. To secure the tube onto the frame of the Ender-3, the
existing mounting holes of the extruder head on the X-axis carriage plate are utilized.
The tube holder is designed for the microbore extension set from Joya Medical Supplies,
Arundel. The 3D design cannot be used for other tube extension models. The Tube
Holder exists in two parts. The bottom part is attached to the X-axis Carriage Plate, and
the top part is magnetically attached to the bottom part.

Step 9.1: Insert magnets into Tube holder 

Before installing the Tube Holder onto the X-axis Carriage Plate, insert four magnets into
the holes provided on the 3D-printed parts.
First, place the two parts as shown in Figure 47 with the inside facing forward. Before
inserting the magnets into the holes, ensure that the parts do not repel each other when
they are put together. Therefore, take two disc magnets that attract each other and separate them. Place each of them next to the opposite hole of the other part so that the
surface that was separated from one faces the front. Do the same with the other two
magnets.
Add super glue to one of the holes and insert the magnet without changing the orientation. Let the glue dry (NOTE 1). Repeat this process for the other three magnets



Step 9.2: Secure the syringe with the tube

Connects the syringe to the female luer connector of the tube. But before connecting luer
lock to the syringe (see Fig. 48a), insert a 32 mm Bulldog Clip onto the tube (see Fig.
48b, NOTE 2). 



NOTE 2 The Bulldog Clip can only be inserted into the tube from the female luer connector side, as the male luer connector has a larger dimension and will not fit through
the clip.

Step 9.3: Attach the Tube Holder to the X-axis Carriage Plate (**_Note: step 9.3 can be skipped if replicating the updated design, as the Tube Holder will be glued to a different mount_**)

The Tube Holder utilizes the mounting holes on the X-axis Carriage Plate circled in orange in Fig. 49a. Insert the two grind-down M3 countersunk screw heads from Step 4.3
into the bottom part of the Tube Holder and tighten it onto X-axis Carriage Plate as shown
in Fig. 49b. 



Step 9.4: Attach Bulldog Clip to the frame

Attached the tube to the frame with a 32 mm Bulldog Clip (see Fig. 50) to prevent the
tube from interfering during the dispensing process. This reduces the uncontrolled movement during the needle's X- and Z-axis movement. 



Step 9.5: Secure the tube and needle with the Tube Holder

Before attaching the tube into the tube holder, insert the needle into the male luer connector of the tube and secure it by tightening the rotating collar. Figure 51a shows that
the male luer connector only fits into the Tube Holder if the needle is firmly connected to
the connector. Insert the male connector into the bottom and attach the Tube Holder's
top part magnetically (see Fig. 51b).



**Step 10: Adjusting the Z-axis limit switch** 
The limit switches are sensors and are installed at the start of each of the X-, Y-, and Zaxes. The limit switches for the X- and Y- axes do not need to be adjusted. If a well plate
is placed on the platform of the Ender-3, the starting point of the Z-axis changes and the
limit switch must be adjusted. Without this adjustment, the dispensing head can drive
into the well plate and be damaged.
First, loosen the two M3 screws from the T-nuts on the Z-axis limit switch. The limit switch
can now slide up and down the rail without any obstacles. There are two ways to adjust
the height of the switch. First, measure the height of the well plate and move the switch
up by this height and tighten the screws again. The second possibility is to use a well
plate. Place the well plate to the position shown in Figure 53 and if the orange circled
part on the limit switch touches the well plate edge, tighten the screws again. 





After setting the Z-axis limit switch, the electronics box can finally be closed. As explained
in Step 4.4, the cable of the Z-axis limit switch plugged into the main board must use the
modified opening. Otherwise, there will be increased tension on the wires. To close the
cover of the motherboard, screw the three M3 screws back in.

NOTE 1 Remove well plate after Z-axis limit switch have been adjusted.

**Step 11: Install Well Plate Frame**

The final Step to complete the assembly of PADL (see Fig. 54) is to place the Well Plate
Frame on the hotbed.
The Well Plate Frame is divided into four parts that fit into each other like a jigsaw puzzle.
A Well Plate and two tubes with a diameter of 27 mm can be inserted into the holes
provided (see Fig. 54).



NOTE 1 The height of the reservoir tubes is considered in the G-code therefore there is
no need to adjust the Z-axis limit switch.

# Part 3: Assembling the updated design (tool-switching mechanism and circuit, waterproofing techniques)
Updated PADL Liquid Handler Assembly Instructions



A) Overview of the final design, including the tool-switching mechanism and circuit, syringe pump, clamp, and control panel and stand. B) The final design of the waterproofing measures, including the extension of the control panel and power box. Note that the waterproofing measures were implemented on Sukukumar’s PADL (2023) for testing purposes, and hence are not part of A). 

**Step 0**

Ensure access to a 3D printer equipped with PLA and TPU filaments. Note that specific settings are necessary to produce 3D parts with a smooth finish, minimising the need for extensive filing. We utilised 3D prints conforming to the standard 1.75mm diameter printing specifications, employing the "eSUN orange PLA+ filament" brand, which was supplied in a 1kg spool.

**Step 1**

Visit the GitHub page and download all STL files and Laser cut files necessary to replicate this project https://github.com/nkonstantini/Robotics-to-perform-biomedical-experiments-capstone-project  

**Step 2**

Assemble the 3D components, including the syringe pump and well plate frame. For detailed instructions, please refer to Part 2 of Sukukumar's work from 2023.





**Step 3**

Assemble the 3D components: tool holder and clamp system. Use a tapping set to thread the holes in the clamp. Next, use an Allen key and two M3x10 screws to secure the clamp onto the x-carriage plate. 



Begin by adhering the magnets, aligning them according to the specified magnetic polarity, using super glue. Next, affix two 3mm acrylic plates as demonstrated above, utilising double-sided tape. Attach the tool holder with the small magnets to the mounts, as illustrated below. This can be done by applying Zap-A-Gap bonder to the inside surfaces of the tool holder, and placing the original syringe tool mount inside. Once the tool, such as the needle, is inserted, use orange tape to secure it, preventing both tool slippage and interference with the larger magnet mechanism.



**Step 4**

Please visit the dedicated Reddit page created for this purpose to find instructions on constructing the circuit for the additional stepper motor (integrating a fifth stepper motor with the Ender 3 motherboard 4.2.2).

https://www.reddit.com/r/ender3v2/comments/qzxsok/i_added_a_5th_stepper_driver_to_the_stock/  

The remaining part of step 4 consists of direct quotes from the Reddit page “How To Add Another Stepper Driver to the Stock Creality 4.2.2 Main Board”.

_How To Add Another Stepper Driver to the Stock Creality 4.2.2 Main Board_
_Without soldering directly on the mainboard!

_Last Revised: 3/17/2023 - willsside_

_Always be careful when working with electronics and high voltages. All actions described in this tutorial are performed at your own risk. The author is not responsible for any damages._ 

_This tutorial will describe how to add an additional stepper driver to the stock Creality 4.2.2 board. The stock board that is shipped with most Ender 3/Pro/V2s have four integrated stepper drivers onboard (typically TMC2208). These are fine for a standard printer, however the maximum of four stepper drivers are a limitation when new features are desired, such as a second extruder or a second z axis stepper motor._

*One way to do this is to solder new wires to unused pins on the main integrated circuit (IC) onboard the 4.2.2 board (STM32F103RET6). However, soldering on the tiny pins, or on other tiny surface mounted components is very difficult and could cause damage to your mainboard. Thankfully, there are a few extra headers on the board that are unused and directly connect to pins on the main IC! This means that we don’t need to get a soldering iron anywhere near the main board; adding a stepper driver may be as simple as plug-and-play! (assuming changes in Marlin)
For this tutorial, I’ll be adding a second z-axis stepper. However, the tutorial is essentially the same for driving any other type of stepper (2nd extruder, 2nd x-axis, etc).*

*Note, this mod has been successful in adding another stepper driver for the following main boards:* 

*Creality 4.2.2*

*Creality 4.2.7*

_SKR Mini E3 V2.0 (link to more info)_

*Theoretically, this mod can be applied to any main board with unused and easily accessible pins!*

**_Materials:_**

_Creality 4.2.2 board (should also work with 4.2.7 board)_

_Spare TMC2208/2209 Driver_ 

_100µF 35v Capacitor_ 

_Dual Z Stepper kit_ (**Note: not required for the PADL v2 design**)

_42-34 Stepper Motor (42mm x 42mm x 34mm)_

_Threaded Rod (365mm)_ (**Note: not required for the PADL v2 design**)

_Z coupler_ (**Note: not required for the PADL v2 design**)

_If you really want a plug and play experience, you can get these:_

_Dupont wires (breadboard wires)_

_Stepper JST to Dupont wires_

_Stepper Driver Breakout Board_

**_Wiring:_**

_On the Creality 4.2.2 board there are 4 pins right above the LCD port that are unused and exposed (they might be covered with hot glue)._ 



_If there are no headers on these 4 pins (just holes), you will need to solder wires or headers on the board. However, I think most boards come with these pins._ 



_Two of these pins are VCC and GND (3.3 V and Ground, respectively) and the middle two are SWDIO and SWCLK. You don’t have to know what they are, but what’s important is that they are directly connected to pins PA13 and PA14 on the mainboard IC! Therefore, we can reprogram the chip through Marlin firmware to command another stepper driver through these two pins._

_For this case, we will be using our additional TMC2208 driver in STANDALONE mode: therefore NOT in UART mode. This means that Marlin can’t use UART to talk to the driver to change max current or for fancy features like linear advance. However, this is okay because all four integrated TMC2208s in this Creality 4.2.2 board are already in STANDALONE mode. This also simplifies the wiring, because we will only need two pins to communicate with the driver._
	
 _(If you want to use UART, u/LookAtDaShinyShiny has a great tutorial for unlocking the functionality on the 4.2.2 board too! I wish I’d seen this before I did my mod, it would have saved me a ton of time!)_
 
**_Wiring Diagram:**

_The TMC2208 stepper driver requires only two data pins (STEP and DIR) for use in STANDALONE mode. Along with those pins, it requires an I/O voltage (VCC) and ground (GND). You can use dupont wires to directly connect these._
 
 

_In addition, the driver requires the motor voltage (24V). This can be done with dupont wires as well, but I’d recommend using some thicker wire (like 22 AWG) to be safe. The capacitor is to smooth out fluctuations in the 24V line and it should be installed as close to the stepper driver as possible. NOTE: In STANDALONE mode (without UART), the MS1 and MS2 pins need to be set high (VCC) so that the steps are assumed to be 16 microsteps per step. Other configurations are located on the TMC2208 datasheet (3.4 Configuration Pins). In addition, I set the ENABLE pin to be always set to GND. This means that this driver is always enabled (cannot be disabled)._ 
	
_Personally, I decided to solder the driver to a piece of prototyping board and solder down the wires too. You can also use a tiny breadboard if you don’t want to solder. Triple check your connections!_



_I used a large breadboard first to test functionality_

_Now, it is important to make sure that your stepper motor wires are correct. The four pins below must be connected to the correct 4 pins on the stepper motor. From the picture below, M1A and M1B should be connected to RED and GRN (Wires 1 and 2) and M2A and M2B should be connected to YEL and BLU (Wires 3 and 4)._ 

_NOTE: If you get these pins wrong, your stepper motor may make some truly terrible sounds and vibrate. As far as I know, the stepper motors are NOT damaged from these vibrations. It seems that different manufacturers may have different coil configurations. No worries though, you have two options_

_1. Use a multimeter to probe the pins on the stepper motor and see which two have continuity (use the continuity mode on your multimeter). Two continuous pins should connect to M1A and M1B, and the other two pins should be on M2A and M2B._ 

_2. If you don’t have a multimeter, you can simply try different combinations. Try to switch two wires at a time (start with inner two and outer two) and try to run the motor briefly._

_If you’re using the dupont to JST stepper wires, follow each wire to make sure that they are going to the correct pins. If they are not, it is very easy to swap pins on dupont connectors. Also, if the stepper motor is moving the wrong way, you can either switch the M2 and M1 pins OR change the direction in software (Marlin). Software is much easier._



_*** This wiring may NOT work for you! Read the NOTE above if it doesn’t work! ***_

_Last but not least, make sure that no pins can short! For my soldered solution, I put electrical tape all along the bottom of the perf board. This prevents a short if the board is touching the printer’s metal housing. If you have a breadboard, you will probably be fine, but just look out for potential shorts! A multimeter with connectivity checks helps a ton._

_After you’ve triple checked your connections, you’re done with wiring! Congrats! Now time for firmware...._

**Firmware Changes in Marlin:**

Refer to the ‘Marlin’ folder for instructions on how to modify the firmware for the PADL device.

**_Testing the New Stepper Driver / Motor_**
_Now that you’ve compiled your new firmware and placed the .bin file on the printer’s SD card, it’s time to test!!!_

_IMPORTANT: Triple check your connections and make sure there are no shorts. We don’t want to release the magic smoke on your mainboard or your extra stepper driver; there’s no way to put it back. Also, make sure to first unscrew the original z-stepper motor’s coupling to the threaded rod. This will make sure that the steppers don’t fight each other if the new stepper motor turns the wrong direction._

_When you are confident that the connections are correct, reinsert your SD card with the new firmware and turn on the printer. You should hear the new stepper motor go “THUNK” as it is enabled automatically (nothing wrong with the sound). Once you’ve confirmed that nothing has broken, you can start to test! Now, go into your printer’s menu and command the printer to move up or down 5 mm. If the second stepper motor starts moving, you did it!!!_

_Before you reinstall the original stepper motor, make sure that your stepper moves exactly how much you command it to. Get a ruler and check that the x-gantry moved up 5 mm. If it is moving double the commanded amount (10 mm), make sure that your microsteps are set correctly (refer to MS1 and MS2 in the Wiring section)._

_Finally, reinstall the original z-stepper motor coupler and command the z-axis to move up or down 5 mm. If both are moving fine (and at the same speed), congrats!!! You officially have added a new stepper driver to the stock Creality 4.2.2 board!!!_

**_Error Modes:_**
_Nothing fried, but the stepper motor doesn’t move when I command it.: 
_Check your wiring (make sure the STEP and DIR pins aren’t flipped: if they are, you can just swap the pins in the pins_CREALITY_V4.h file)_

_Check your firmware:_

_My stepper motor is moving twice as fast / slow as the original stepper motor: Your microsteps are probably set incorrectly. On the Creality 4.2.2 board, the drivers are set to 16 microsteps per step. You will have to make sure that the MS1 and MS2 pins are correctly configured (look at the wiring diagram)._

_My stepper motor is moving in the opposite direction that it should be: In Marlin you can change the direction of the stepper motor in the firmware by uncommenting:  #define INVERT_Z2_VS_Z_DIR In configuration_adv.h. OR: You can swap the M1(a/b) and M2(a/b) pins on the dupont wires connected to the stepper driver_

**_Finishing Touches_**

_Don’t forget to change the reference voltage on the new stepper motor! Because we are in STANDALONE mode, the stepper current cannot be changed in firmware. You will need to change the reference voltage via the screw on the driver itself. Teaching Tech has a great  video describing how to do this (I’d recommend doing it to your integrated drivers as well)._ 

_Where do you put the extra stepper driver?? I actually found just enough space to the left of the main board and hot glued the new stepper driver there. However, if you use one of the small breadboards you may need to find a place outside the mainboard compartment to leave the stepper. Just make sure that the heatsink has some airflow to cool it down and mount it somewhere safe so it doesn’t short!_



**Step 5**

Solder the components together, assemble the parts, and waterproof the newly added fifth stepper motor.





Following the soldering process, secure the solder board onto the top side of a 6mm acrylic plate measuring 33*36 mm using four M5 screws and a hot glue gun. Additionally, use double-sided tape at the bottom to stabilise it with the 3D prints, ensuring the wires do not come into contact with metal to prevent electrical hazards.

**Step 6**

Assemble the 3D components, cut the V-rails, drill holes, and integrate a belt system along with the mounts and stepper motor.



We resized the V-rails and drilled holes using a drill press in the metal workshop for the longer V-rails. This enabled us to securely attach the two tool mounts using long screws. Grub screws were used to fasten the mounts together with the GT2 pulley, while nyloc nuts prevented loosening during rotation. Washers were added to ensure the screws remained tight and stable when the stepper motor was in motion.

For the shorter screws, we threaded some holes using four M5 screws and four M2.5 screws to firmly secure the stepper motor mounts. Subsequently, we employed a belt tensioner, as demonstrated below, along with a screw to further tighten and maintain the belt tension consistently. To anchor the V-rails to the printer frame, eight additional holes were drilled on the side. These were secured using rivet screws and eight M5 screws for stability.



A: https://cults3d.com/en/3d-model/tool/gt2-belt-tensioner-create_tec  

B: https://www.thingiverse.com/thing:1071695/comments

**Step 7**

Other waterproofing approaches

The initial step involved sealing the motherboard case vents using water-resistant and conductive aluminium sheets, as demonstrated in Figure B), to prevent water ingress while also acting as a heatsink. Furthermore, the removal of the motherboard fan, as indicated in Figure C), curtailed any active influx of humid air, thereby augmenting the motherboard's protection.



Using chemically resistant butyl rubber gloves, a thin layer of the aerosol was applied to the underside and top of the motherboard within a fume hood. Prior to application, all wires and connections were removed, and any connection ports and capacitors were covered with electrical tape, according to Figure A).



A blunt needle was used to apply and spread a small amount of conductive grease over all active ports in the motherboard, as well as the ports of the wires connected to the stepper motors. All the unused ports, including the micro USB and microSD card ports, were covered with electrical tape, as shown in the Figure below.



Acrylic plates have been applied to the exposed ends of the v-rails to protect the interiors from corrosion, as depicted in Figures A) and B). These plates were designed and cut using a laser-cutting machine. While aluminium does not rust, due to the formation of a stable layer of aluminium oxide that shields the metal from reacting with water, it is still subject to corrosion over long periods of time.



The final motherboard waterproofing measure was to re-attach the motherboard to its housing, secure the lid back on, and secure the gaps where water could ingress with electrical tape. The areas that were taped are shown in the Figure below. Electrical tape also acts as an insulator to protect against any current leakage.



The Extension Screen Cable (200cm) and Extension Power Cord (60cm) are utilised as replacements for the original Ender-3 wires. This substitution is not only due to the lack of waterproofing in the original power and screen components but also for enhanced operational convenience. The extended cables facilitate easier access to the power source, allowing seamless on-off control, and providing the flexibility to choose when to activate the G-code stored in the SD card.



**Step 8**

Heat control 

Given the potential for prolonged operation of the PADL within an incubator maintained at 37°C, effective heat management is essential to prevent the stepper motors from overheating and experiencing damage. This was of particular concern for the tool-switching stepper motor, which cannot idle to dissipate heat in between tool changes.

The conductive thermal grease is combined with double-sided tape to aid in the efficient dissipation of heat from the stepper motors.


 


**Step 9**

Integrate all components into a unified assembly. 



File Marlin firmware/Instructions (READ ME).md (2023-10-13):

# Instructions for reflashing the Marlin firmware and modifying the firmware
If you *do not* wish to modify the firmware yourself, follow the instructions for **Part A**.

If you wish to modify the firmware, follow the instructions for **Part B and Part C**

## Part A: Reflashing the firmware
1. Download the ‘final_firmware.bin’ file provided in the Marlin firmware folder (note that this is derived from Marlin bugfix 2.1x version on on Marlin's github page)
2. Copy the .bin file onto a blank microSD card (**Note: reflashing will NOT work if the microSD card is not blank**)
3. Eject the microSD card
4. Insert the microSD card into the Ender-3’s microSD port
5. Turn on the printer. If the printer prompts you to update or reset the EEPROM.dat, click yes
6. The printer firmware has been reflashed. Check that there is an ‘A’ axis you can control.

## Part B: Downloading the required software
Note that the following video is a very useful guide and **should be watched prior to completing Part B and Part C**: [Updated Marlin firmware setup guide - VS Code and Auto Build Marlin](https://www.youtube.com/watch?v=eq_ygvHF29I)

1. Install VS code 
2. Open VS code. Open the ‘Extensions’ tab on the left-hand side of the screen. Using the search bar, search for ‘Auto Build Marlin’. Click the blue install button on the bottom right of the icon (should appear in place of the ‘copy’ and ‘settings’ button in the screenshot below)



3. Repeat step 2, but this time search for and install ‘PlatformIO’ 
4. Open [Marlin's GitHub page](https://github.com/MarlinFirmware/Marlin). Click on the ‘Code’ tab, then click ‘Download zip’



5. Repeat step 4 for the configuration files located on this page. 
7. Unzip the folders ‘Marlin-bugfix-2.1.x’ and ‘Configurations-bugfix-2.1.x’
8. From the ‘Configurations-bugfix-2.1.x’ folder, go to ‘config’ -> ‘examples’->’Creality’->’Ender-3’->’CrealityV422’ and copy all files in this folder
9. Open the ‘Marlin-bugfix-2.1.x’ folder in a new window. Go to ‘Marlin’ and paste all the copied files. Click ‘replace duplicate files’ if prompted. This step configures Marlin for the Ender-3.
10. You are now ready to open the files mentioned in part C in VS Code and update the firmware.

## Part C: Modifying the firmware
Open the following files in VS code, and search for the following lines using Control + F. If the line doesn't exist, append it to the relevant section. For additional assistance, consult the following GitHub page: https://github.com/DerAndere1/Marlin/wiki 

### Configuration.h: (Marlin-bugfix-2.1.x/Marlin/)
#define I_DRIVER_TYPE TMC2208_STANDALONE

#define I_ENABLE_ON 0

#define I_MIN_POS 0

#define X_BED_SIZE 240 //changed from 235 to 240 to account for tool changing

#define I_MAX_POS X_BED_SIZE

#define I_HOME_DIR -1

#define DEFAULT_AXIS_STEPS_PER_UNIT   { 80, 80, 400, 80, 93}

#define DEFAULT_MAX_FEEDRATE          { 500, 500, 5, 60, 25}

#define DEFAULT_MAX_ACCELERATION      { 500, 500, 100, 500, 5000}

#define HOMING_FEEDRATE_MM_M { (20*60), (20*60), (4*60), (20*60)}

#define INVERT_I_DIR false //direction of turning doesn’t matter

#define DISABLE_I // disable when not in-use as disable_idle_I (note: this command does not appear to work in the current design)

### Configuration_adv.h (Marlin-bugfix-2.1.x/Marlin/)
#define MANUAL_FEEDRATE { 50*60, 50*60, 4*60, 50*60, 2*60} // (mm/min) Feedrates for manual moves along X, Y, Z, E from panel

Uncomment the following line in Idle stepper shutdown section:

#define DISABLE_IDLE_I // (note: this command does not appear to work in the current design)

### pins_CREALITY_V4.h (Marlin-bugfix-2.1.x/Marlin/src/pins/stm32f1/pins_CREALITY_V4.h)
Type the following:

#define I_ENABLE_PIN                       PC3 //(connect to ground to always enable)

#define I_STEP_PIN                         PA14 //SWCLK (STEP - pulled low)

#define I_DIR_PIN                          PA13 //SWIO  (DIR - pulled high)

#define I_STOP_PIN 0 //not required for our application: we are not actually creating a new axis

Comment out:

// #if HOTENDS > 1 || E_STEPPERS > 1

//   #error "Creality V4 only supports one hotend / E-stepper. Comment out this line to continue."

// #endif

**When the above changes have been made**:
1. Open Auto Build Marlin
2. Choose the environment that corresponds to your CPU type (to find out your CPU type, open up the motherboard case and look at the writing on the CPU. This text should correspond with one of the options listed in the environments section.
3. Click the 'Build' button next to the environment chosen. The next time you modify the firmware, this selection will be highlighted in green.



4. If successful, the folder the new build has been downloaded to will pop up on your screen, and the .bin file generated will be highlighted. Move this file to an empty microSD card, and follow the instructions from **Part A** to reflash your printer

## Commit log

2023-10-05 Create stepper motor circuit.md
2023-10-13 Add files via upload
    Note that if you're replicating this project, ensure you print out 2 of the tool_frame_mount_3magnets.stl files (if you want 2 docks)
    [Tool_frame_mount_3magnets.stl, clamp_update.stl]
2023-10-13 Source: (stratop80, 2023) (https://www.thingiverse.com/thing:1071695/files)
    Print 2 of the tensioner body component
    [GT2_belt_tensioner_body-1.STL, GT2_belt_tensioner_clip-1.STL]
2023-10-16 All the laser cut parts used in the design, in 3 different file formats (pdf, dxf, cdr)
    [laser_cut.dxf]
2023-10-23 Create Bill of materials.md
2023-10-23 Update Bill of materials.md
2023-10-23 Bill of materials and list of tools, including cost
2023-10-23 Bill of materials and tools required for build, including cost
2023-10-28 All the CAD files (.f3d) used in our design
    [Tool Change - Clamp.f3z]
2023-10-29 Sample code blocks for tool switching using both mounts
2023-10-30 Stepper motor bracket file
    [A_axis_stepper_motor_mounting_bracket.f3d]
